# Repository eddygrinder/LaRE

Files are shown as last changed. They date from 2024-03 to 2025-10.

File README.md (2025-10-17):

## Objectives
This project is an integral part of the Master’s Dissertation entitled “LaRE – Expandable Remote Laboratory”.
It implements and manages a remote laboratory for electronics education, designed as a viable alternative to VISIR, with the additional commitment of being an open-source project, accessible to any educational institution regardless of geographical location.

The board matrix, the core element of the system, was developed based on a software-controlled architecture independent of proprietary platforms, ensuring that the system can be used without commercial licenses.

However, due to the current lack of support for the pyVirtualBench library on Linux systems and ARM architectures, the implementation of LaRE remains dependent on Windows systems — a factor that limits its adoption in more versatile and low-cost educational platforms.
Nevertheless, the modular architecture of LaRE enables future expansions and adaptations to different pedagogical contexts.

This dissertation partially fulfills the requirements defined in the Course Unit of Dissertation/Thesis of the 2nd year of the Master’s Degree in Electrical and Computer Engineering, specialization area in Automation and Systems.

## System Overview

The LaRE system is composed of:

* **PC (Server)** – runs a Flask-based Python web server.  
* **Raspberry Pi 5** – controls the relay matrix for switching circuits.  
* **NI VirtualBench (VB-8012)** – handles voltage, current, and waveform measurements.  
* **Web Interface** – implemented in HTML, CSS, and JavaScript for user interaction.  

Communication between the PC and Raspberry Pi is handled via **network sockets**, ensuring a simple and robust client–server connection.

## Helpful Resources
* [YouTube – Tech With Tim Flask Tutorial](https://www.youtube.com/watch?v=dam0GPOAvVI)  
* [Flask Official Documentation](https://flask.palletsprojects.com/en/stable/)  
* [pyVirtualBench Library (Armstrap)](https://github.com/armstrap/armstrap-pyvirtualbench)  
* [Armstrap Blog Post](http://armstrap.org/2015/07/27/pyvirtualbench-controlling-five-instruments-from-a-single-python-application/)

## Requirements (Windows Only)
* [NI VirtualBench hardware](http://www.ni.com/virtualbench/)
* [VirtualBench driver >= 1.1.0](https://www.ni.com/en-us/support/downloads/drivers/download.virtualbench-software.html#324215)
  Be sure to check "ANSI C Support" during installation.
    NiInstaller
* [Python >= 3.4](https://www.python.org/downloads/).  You will need 32-bit Python support to work with the NI-provided drivers.

## Dependencies
To install the Python dependencies:
* pip install -r requirements.txt

## Licensing
This project is distributed under the terms of the GNU General Public License, version 3 (GPLv3).
It includes portions of code adapted from: armstrap/armstrap-pyvirtualbench, licensed under the MIT License (© 2015 Charles Armstrap).

See the files LICENSE and THIRD_PARTY_LICENSES.txt for full details.

## Author
Eduardo Ramalhadeiro
Master’s in Electrical and Computer Engineering – Automation and Systems
Instituto Politécnico do Porto (ISEP)
© 2025

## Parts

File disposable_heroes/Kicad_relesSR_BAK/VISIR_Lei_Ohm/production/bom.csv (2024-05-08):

Designator | Footprint | Quantity | Value | LCSC Part #
C1 | C_Disc_D5.0mm_W2.5mm_P2.50mm | 1 | 0.1uF
J1 | PinHeader_2x20_P2.54mm_Vertical | 1 | Raspberry PI5
J10 | PinHeader_1x03_P2.54mm_Vertical | 1 | Amperimetro+
J11 | PinHeader_1x03_P2.54mm_Vertical | 1 | Amperimetro-
J2 | PinHeader_1x02_P2.54mm_Vertical | 1 | Fonte dc_VB
J3 | PinHeader_1x02_P2.54mm_Vertical | 1 | Fonte 12V
J4 | PinHeader_1x03_P2.54mm_Vertical | 1 | Voltimetro+
J5, J6, J7, J8 | PinHeader_1x20_P2.54mm_Vertical | 4 | Ext_OUT_PI
J9 | PinHeader_1x03_P2.54mm_Vertical | 1 | Voltimetro-
K1, K2, K3 | RELAY8_3572-1220-053_COM | 3 | 3572-1220-123
K4, K5, K6, K7, K8 | SIP_3570-1331_COM | 5 | 3570-1331-123
MES1 | PinHeader_1x02_P2.54mm_Vertical | 1 | Voltmeter_DC
MES3 | PinHeader_1x02_P2.54mm_Vertical | 1 | Ammeter_DC
R1 | R_Axial_DIN0207_L6.3mm_D2.5mm_P15.24mm_Horizontal | 1 | R1
R2 | R_Axial_DIN0207_L6.3mm_D2.5mm_P15.24mm_Horizontal | 1 | R2
R3 | R_Axial_DIN0207_L6.3mm_D2.5mm_P15.24mm_Horizontal | 1 | R3
U1 | DIP-16_W10.16mm | 1 | 74HC595N_112 | 74HC595N,112
U2, U3 | DIP-16_W10.16mm | 2 | ULN2003

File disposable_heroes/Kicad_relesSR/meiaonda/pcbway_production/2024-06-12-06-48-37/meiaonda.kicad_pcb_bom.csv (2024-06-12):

designator | quantity | value | pack | mpn | mount_type
C1 | 1 | 10uF | CP_Radial_D6.3mm_P2.50mm |  | tht
C2 | 1 | 100uF | CP_Radial_D6.3mm_P2.50mm |  | tht
C3, C4 | 2 | 0.1uF | C_Disc_D5.0mm_W2.5mm_P2.50mm |  | tht
C6 | 1 | 10uF | CP_Radial_D5.0mm_P2.00mm |  | tht
D1 | 1 | 1N4007 | D_DO-41_SOD81_P10.16mm_Horizontal |  | tht
D2 | 1 | B250C2300-1500A | Diode_Bridge_19.0x3.5x10.0mm_P5.0mm |  | tht
F1 | 1 | Fuse | Fuseholder_Cylinder-5x20mm_Stelvio-Kontek_PTF78_Horizontal_Open |  | tht
H1, H2, H3, H4 | 4 | MountingHole | MountingHole_3.2mm_M3 |  | tht
J2 | 1 | PI_config | PinSocket_1x06_P2.54mm_Vertical |  | tht
J3 | 1 | Power Sources | PinSocket_1x06_P2.54mm_Vertical |  | tht
J4 | 1 | Signals | PinSocket_1x06_P2.54mm_Vertical |  | tht
K1, K2, K3, K5, K6, K7, K8, K9 | 8 | 3572-1220-123 | RELAY8_3572-1220-053_COM |  | tht
K10, K11, K12, K13, K4 | 5 | 3570-1331-123 | SIP_3570-1331_COM |  | tht
R1, R3 | 2 | 1K | R_Axial_DIN0207_L6.3mm_D2.5mm_P15.24mm_Horizontal |  | tht
R2 | 1 | 4.7K | R_Axial_DIN0207_L6.3mm_D2.5mm_P15.24mm_Horizontal |  | tht
U1, U3 | 2 | 74HC595N_112 | DIP-16_W10.16mm | 74HC595N,112 | tht
U2, U4 | 2 | ULN2003 | DIP-16_W10.16mm |  | tht

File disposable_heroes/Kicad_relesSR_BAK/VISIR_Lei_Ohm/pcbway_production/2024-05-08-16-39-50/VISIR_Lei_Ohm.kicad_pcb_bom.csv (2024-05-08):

designator | quantity | value | pack | mpn | mount_type
C1 | 1 | 0.1uF | C_Disc_D5.0mm_W2.5mm_P2.50mm |  | tht
H1, H2, H3, H4 | 4 | MountingHole | MountingHole_3.2mm_M3 |  | tht
J1 | 1 | Raspberry PI5 | PinHeader_2x20_P2.54mm_Vertical |  | tht
J10 | 1 | Amperimetro+ | PinHeader_1x03_P2.54mm_Vertical |  | tht
J11 | 1 | Amperimetro- | PinHeader_1x03_P2.54mm_Vertical |  | tht
J2 | 1 | Fonte dc_VB | PinHeader_1x02_P2.54mm_Vertical |  | tht
J3 | 1 | Fonte 12V | PinHeader_1x02_P2.54mm_Vertical |  | tht
J4 | 1 | Voltimetro+ | PinHeader_1x03_P2.54mm_Vertical |  | tht
J5, J6, J7, J8 | 4 | Ext_OUT_PI | PinHeader_1x20_P2.54mm_Vertical |  | tht
J9 | 1 | Voltimetro- | PinHeader_1x03_P2.54mm_Vertical |  | tht
K1, K2, K3 | 3 | 3572-1220-123 | RELAY8_3572-1220-053_COM |  | tht
K4, K5, K6, K7, K8 | 5 | 3570-1331-123 | SIP_3570-1331_COM |  | tht
MES1 | 1 | Voltmeter_DC | PinHeader_1x02_P2.54mm_Vertical |  | tht
MES3 | 1 | Ammeter_DC | PinHeader_1x02_P2.54mm_Vertical |  | tht
R1 | 1 | R1 | R_Axial_DIN0207_L6.3mm_D2.5mm_P15.24mm_Horizontal |  | tht
R2 | 1 | R2 | R_Axial_DIN0207_L6.3mm_D2.5mm_P15.24mm_Horizontal |  | tht
R3 | 1 | R3 | R_Axial_DIN0207_L6.3mm_D2.5mm_P15.24mm_Horizontal |  | tht
U1 | 1 | 74HC595N_112 | DIP-16_W10.16mm | 74HC595N,112 | tht
U2, U3 | 2 | ULN2003 | DIP-16_W10.16mm |  | tht

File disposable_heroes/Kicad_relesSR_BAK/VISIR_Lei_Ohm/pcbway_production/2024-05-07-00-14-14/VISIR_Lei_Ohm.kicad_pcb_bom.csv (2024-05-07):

designator | quantity | value | pack | mpn | mount_type
C1, C2 | 2 | 0.1uF | C_Disc_D5.0mm_W2.5mm_P2.50mm |  | tht
H1, H2, H3, H4 | 4 | MountingHole | MountingHole_3.2mm_M3 |  | tht
J1 | 1 | Raspberry PI5 | PinHeader_2x20_P2.54mm_Vertical |  | tht
J2 | 1 | Fonte dc | PinHeader_1x02_P2.54mm_Vertical |  | tht
J3 | 1 | Fonte 12V | PinHeader_1x02_P2.54mm_Vertical |  | tht
J4 | 1 | Fonte 5V | PinHeader_1x02_P2.54mm_Vertical |  | tht
J5, J6, J7, J8 | 4 | Ext_OUT_PI | PinHeader_1x20_P2.54mm_Vertical |  | tht
K1, K2, K3 | 3 | 3572-1220-123 | RELAY8_3572-1220-053_COM |  | tht
K4, K5, K6, K7, K8 | 5 | 3570-1331-123 | SIP_3570-1331_COM |  | tht
MES1 | 1 | Voltmeter_DC | PinHeader_1x02_P2.54mm_Vertical |  | tht
MES3 | 1 | Ammeter_DC | PinHeader_1x02_P2.54mm_Vertical |  | tht
R1 | 1 | R1 | R_Axial_DIN0207_L6.3mm_D2.5mm_P15.24mm_Horizontal |  | tht
R2 | 1 | R2 | R_Axial_DIN0207_L6.3mm_D2.5mm_P15.24mm_Horizontal |  | tht
R3 | 1 | R3 | R_Axial_DIN0207_L6.3mm_D2.5mm_P15.24mm_Horizontal |  | tht
U1, U4 | 2 | 74HC595N_112 | DIP-16_W10.16mm | 74HC595N,112 | tht
U2, U3 | 2 | ULN2003 | DIP-16_W10.16mm |  | tht

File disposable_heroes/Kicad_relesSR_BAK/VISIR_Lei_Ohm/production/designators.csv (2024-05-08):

C1:1
H1:1
H2:1
H3:1
H4:1
J1:1
J10:1
J11:1
J2:1
J3:1
J4:1
J5:1
J6:1
J7:1
J8:1
J9:1
K1:1
K2:1
K3:1
K4:1
K5:1
K6:1
K7:1
K8:1
MES1:1
MES3:1
R1:1
R2:1
R3:1
U1:1
U2:1
U3:1

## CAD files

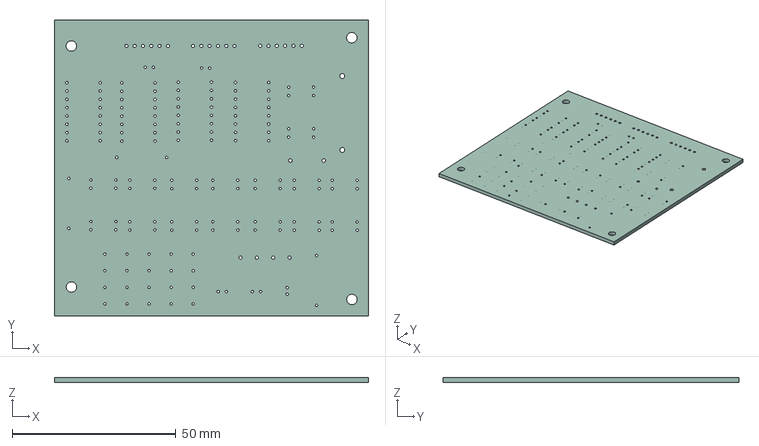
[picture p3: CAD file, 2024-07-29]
disposable_heroes/Kicad_relesSR/meiaonda/meiaonda.step
96.0 x 90.5 x 1.60 mm

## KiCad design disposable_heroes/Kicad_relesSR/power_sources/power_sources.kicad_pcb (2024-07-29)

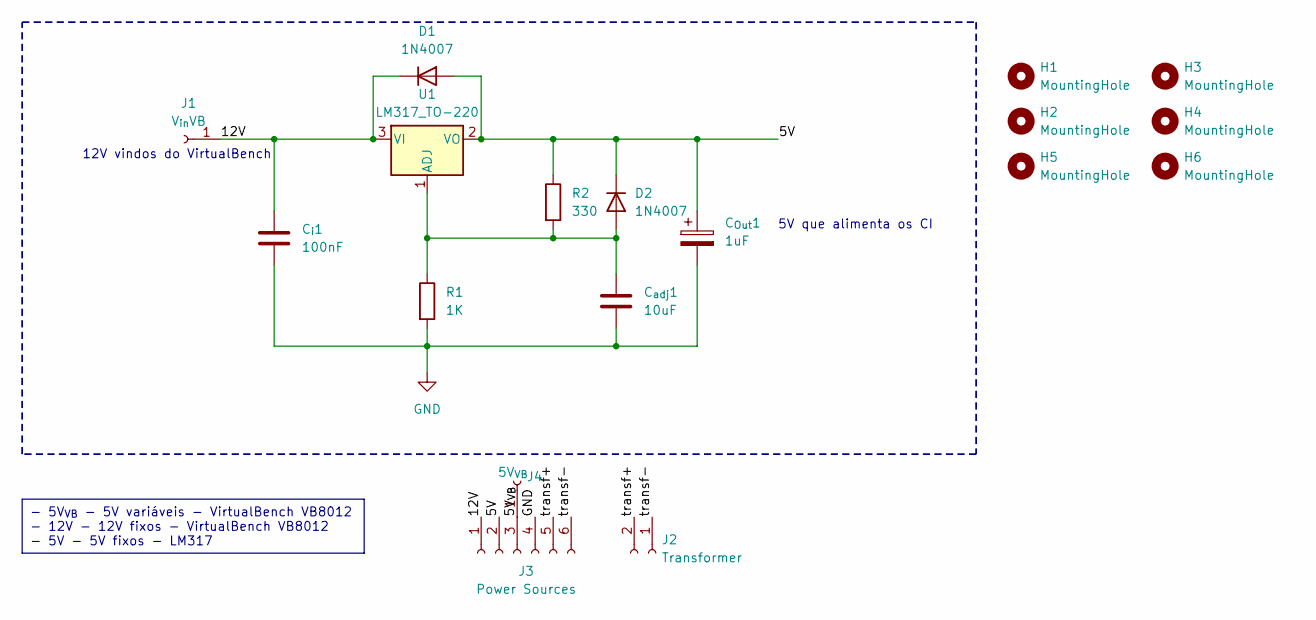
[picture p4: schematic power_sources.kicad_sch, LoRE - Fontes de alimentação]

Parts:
C_{Out}1: 1uF; CP_Radial_D5.0mm_P2.00mm
C_{adj}1: 10uF; CP_Radial_D5.0mm_P2.00mm
C_{i}1: 100nF; C_Disc_D5.1mm_W3.2mm_P5.00mm
D1, D2: 1N4007; D_DO-41_SOD81_P10.16mm_Horizontal
H1, H2, H3, H4, H5, H6: MountingHole; MountingHole_3.2mm_M3
J1: V_{in}VB; PinSocket_1x01_P2.54mm_Vertical
J2: Transformer; PinSocket_1x02_P2.54mm_Vertical
J3: Power Sources; PinSocket_1x06_P2.54mm_Vertical
J4: 5V_{VB}; PinSocket_1x01_P2.54mm_Vertical
R1: 1K; R_Axial_DIN0207_L6.3mm_D2.5mm_P15.24mm_Horizontal
R2: 330; R_Axial_DIN0207_L6.3mm_D2.5mm_P15.24mm_Horizontal
U1: LM317_TO-220; TO-220-3_Vertical

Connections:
/5V: C_{Out}1.1, D1.2 (A), D2.1 (K), J3.2, R2.1, U1.2 (VO)
/5V_{VB}: J3.3, J4.1
/12V: C_{i}1.1, D1.1 (K), J1.1, J3.1, U1.3 (VI)
/transf+: J2.2, J3.5
/transf-: J2.1, J3.6
GND: C_{Out}1.2, C_{adj}1.2, C_{i}1.2, J3.4, R1.2
unnamed: C_{adj}1.1, D2.2 (A), R1.1, R2.2, U1.1 (ADJ)

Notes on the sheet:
- 5V_{VB} - 5V variáveis - VirtualBench VB8012 - 12V - 12V fixos - VirtualBench VB8012 - 5V - 5V fixos - LM317
5V que alimenta os CI
12V vindos do VirtualBench

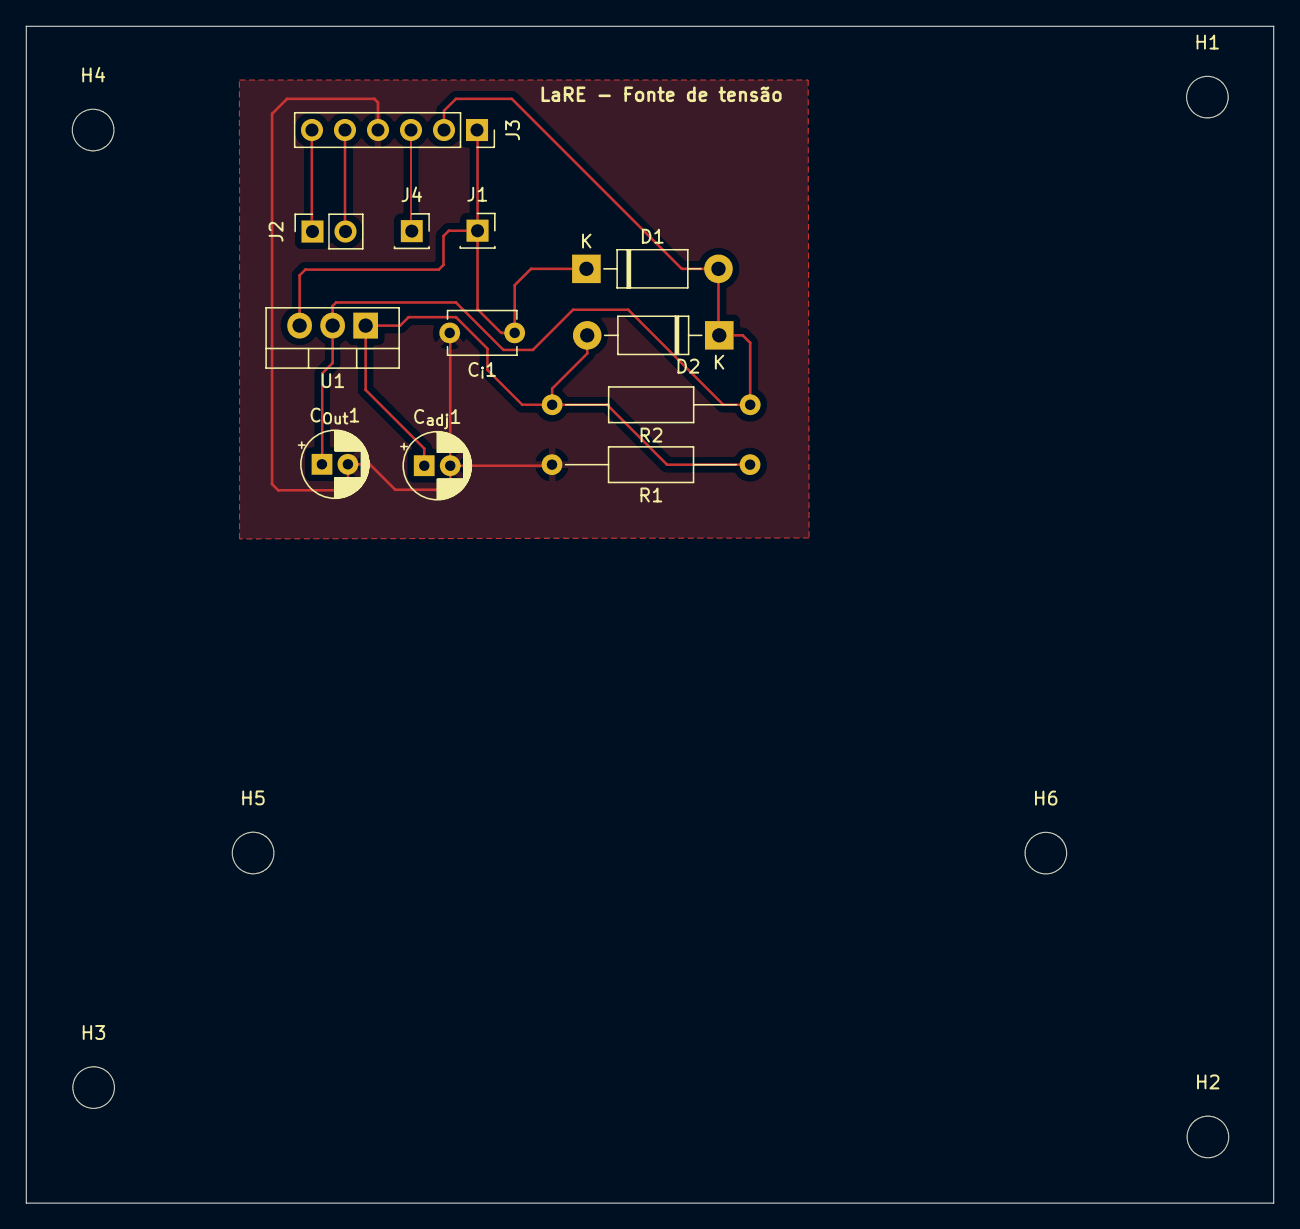
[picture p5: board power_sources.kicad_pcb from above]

Board: 4 copper layers, 96.0 x 90.6 mm, 18 parts (0 on the bottom side), 7 nets.

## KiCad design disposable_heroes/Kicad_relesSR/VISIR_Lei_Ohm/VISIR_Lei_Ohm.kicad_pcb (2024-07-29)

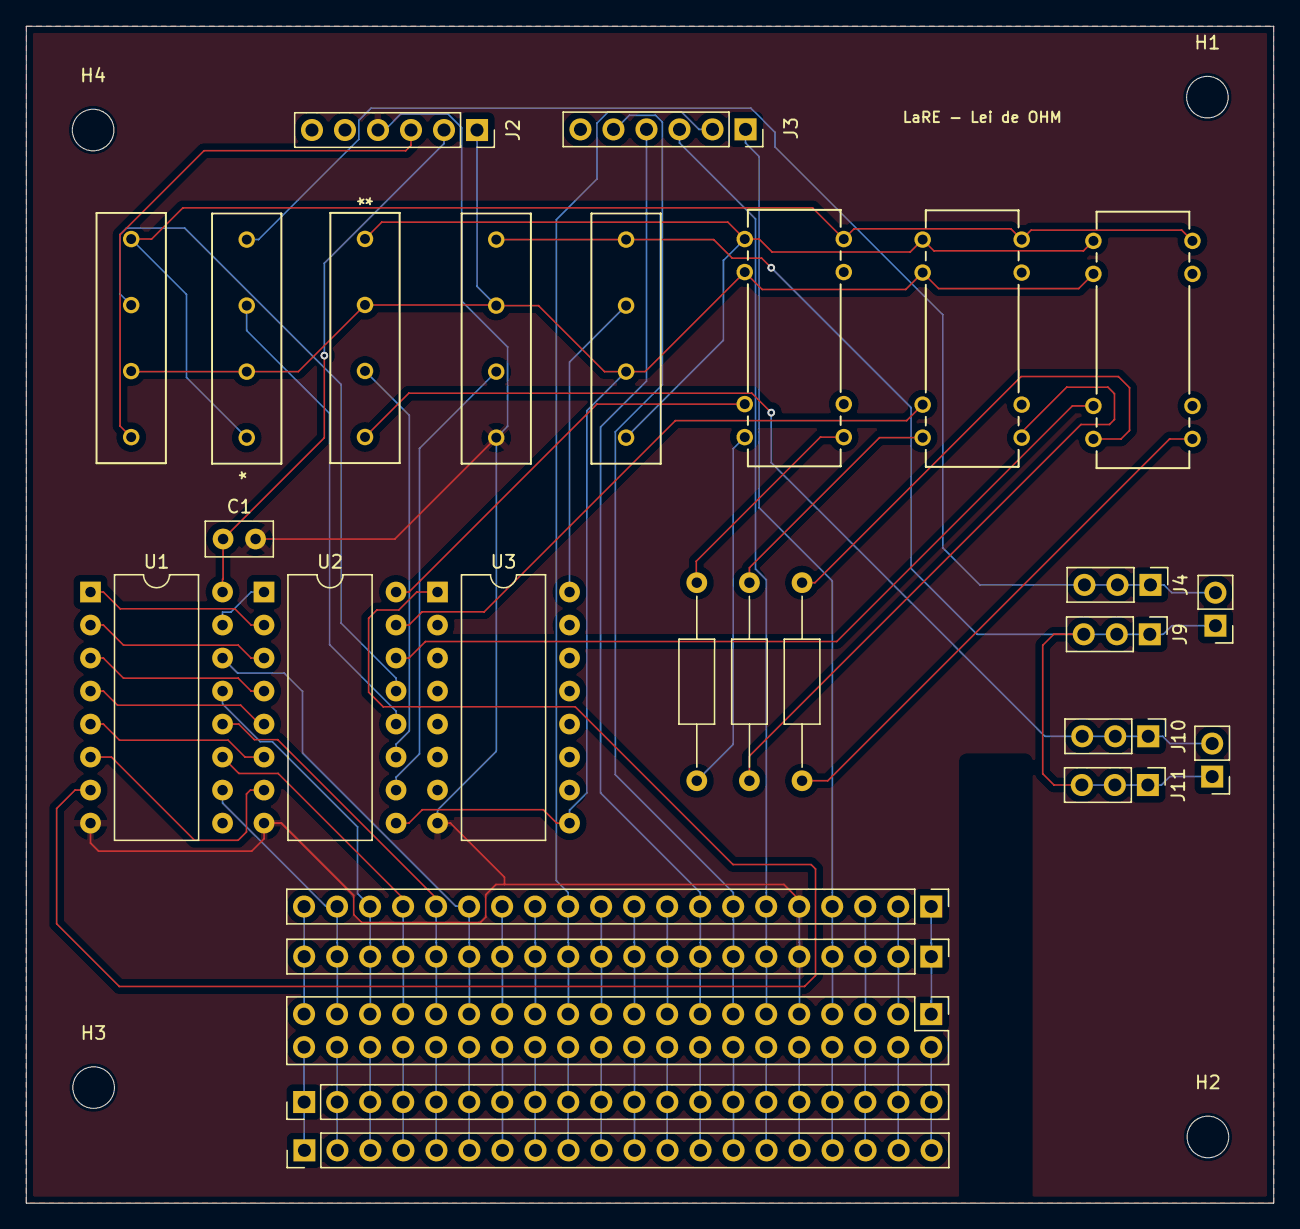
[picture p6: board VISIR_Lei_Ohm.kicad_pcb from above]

Board: 2 copper layers, 96.0 x 90.5 mm, 32 parts (0 on the bottom side), 70 nets.

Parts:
C1: 0.1uF; C_Disc_D5.0mm_W2.5mm_P2.50mm
H1, H2, H3, H4: MountingHole; MountingHole_3.2mm_M3
J1: Raspberry PI5; PinHeader_2x20_P2.54mm_Vertical
J2: Power Sources; PinSocket_1x06_P2.54mm_Vertical
J3: PI_config; PinSocket_1x06_P2.54mm_Vertical
J4: Voltimetro+; PinHeader_1x03_P2.54mm_Vertical
J5, J6, J7, J8: Ext_OUT_PI; PinHeader_1x20_P2.54mm_Vertical
J9: Voltimetro-; PinHeader_1x03_P2.54mm_Vertical
J10: Amperimetro+; PinHeader_1x03_P2.54mm_Vertical
J11: Amperimetro-; PinHeader_1x03_P2.54mm_Vertical
K1, K2, K3: 3572-1220-123; RELAY8_3572-1220-053_COM
K4, K5, K6, K7, K8: 3570-1331-123; SIP_3570-1331_COM
MES1: Voltmeter_DC; PinHeader_1x02_P2.54mm_Vertical
MES3: Ammeter_DC; PinHeader_1x02_P2.54mm_Vertical
R1: R1; R_Axial_DIN0207_L6.3mm_D2.5mm_P15.24mm_Horizontal
R2: R2; R_Axial_DIN0207_L6.3mm_D2.5mm_P15.24mm_Horizontal
R3: R3; R_Axial_DIN0207_L6.3mm_D2.5mm_P15.24mm_Horizontal
U1: 74HC595N_112; DIP-16_W10.16mm
U2, U3: ULN2003; DIP-16_W10.16mm

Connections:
/5V: C1.1, J2.2, U1.16 (VCC)
/5VPower1: J1.2 (5VPower1), J5.20, J6.20
/5V_{VB}: J2.3, K4.1
/12V: J2.1, K1.2, K2.2, K3.2, K4.2, K5.2, K6.2, K7.2, K8.2, U2.9 (COM), U3.9 (COM)
/I_{11}: U1.15 (Q0), U2.1 (I1)
/I_{12}: U1.1 (Q1), U2.2 (I2)
/I_{13}: U1.2 (Q2), U2.3 (I3)
/I_{14}: U1.3 (Q3), U2.4 (I4)
/I_{15}: U1.4 (Q4), U2.5 (I5)
/I_{16}: U1.5 (Q5), U2.6 (I6)
/I_{17}: U1.6 (Q6), U2.7 (I7)
/I_{21}: U1.7 (Q7), U3.1 (I1)
/O_{11}: K1.6, U2.16 (O1)
/O_{12}: K2.6, U2.15 (O2)
/O_{13}: K3.6, U2.14 (O3)
/O_{14}: K4.3, U2.13 (O4)
/O_{15}: K5.3, U2.12 (O5)
/O_{16}: K6.3, U2.11 (O6)
/O_{17}: K7.3, U2.10 (O7)
/O_{21}: K8.3, U3.16 (O1)
/RCLK: J1.31 (GPIO6), J7.16, J8.16, U1.12 (RCLK)
/RCLK_{filters}: J1.11 (GPIO17), J3.3, J7.6, J8.6
/SER1: J1.29 (GPIO5), J7.15, J8.15, U1.14 (SER)
/SER_{filters}: J1.13 (GPIO27), J3.5, J7.7, J8.7
/SRCLK: J1.33 (GPIO13/PWM1), J7.17, J8.17, U1.11 (SRCLK)
/SRCLK_{filters}: J1.7 (GPIO4/GPCLK0), J3.1, J7.4, J8.4
/~OE: J1.35 (GPIO19/PCM_FS), J7.18, J8.18, U1.13 (~OE)
/~OE_{filters}: J1.15 (GPIO22), J3.4, J7.8, J8.8
/~SRCLR: J1.37 (GPIO26), J7.19, J8.19, U1.10 (~SRCLR)
/~SRCLR_{filters}: J1.23 (GPIO11/SCLK), J3.2, J7.12, J8.12
A: K1.14, K2.14, K3.14, K4.4, K5.1
B: K1.1, K2.1, K3.1, K6.1, K8.1
C: J9.1, J9.2, J9.3, J11.1, J11.2, J11.3, K7.1, K8.4, MES1.1 (-), MES3.1 (-)
GND: C1.2, J1.9 (GND), J2.4, J7.5, J8.5, K7.4, U1.8 (GND), U2.8 (GND), U3.8 (GND)
GND1: J1.25 (GND), J7.13, J8.13
GND2: J1.39 (GND), J7.20, J8.20
GND3: J1.6 (GND), J5.18, J6.18
GND4: J1.14 (GND), J5.14, J6.14
GND5: J1.20 (GND), J5.11, J6.11
GND6: J1.30 (GND), J5.6, J6.6
GND7: J1.34 (GROUND), J5.4, J6.4
unnamed: J1.1 (3V3Power1), J7.1, J8.1
unnamed: J1.17 (3v3Power2), J7.9, J8.9
unnamed: J1.4 (5VPower2), J5.19, J6.19
unnamed: J1.27 (GPIO0/ID_SD), J7.14, J8.14
unnamed: J1.28 (GPIO1/ID_SC), J5.7, J6.7
unnamed: J1.3 (GPIO2/SDA), J7.2, J8.2
unnamed: J1.5 (GPIO3/SCL), J7.3, J8.3
unnamed: J1.26 (GPIO7/CE1), J5.8, J6.8
unnamed: J1.24 (GPIO8/CE0), J5.9, J6.9
unnamed: J1.21 (GPIO9/MISO), J7.11, J8.11
unnamed: J1.19 (GPIO10/MOSI), J7.10, J8.10
unnamed: J1.32 (GPIO12/PWM0), J5.5, J6.5
unnamed: J1.8 (GPIO14/TXD), J5.17, J6.17
unnamed: J1.10 (GPIO15/RXD), J5.16, J6.16
unnamed: J1.36 (GPIO16), J5.3, J6.3
unnamed: J1.12 (GPIO18/PCM_CLK), J5.15, J6.15
unnamed: J1.38 (GPIO20/PCM_DIN), J5.2, J6.2
unnamed: J1.40 (GPIO21/PCM_DOUT), J5.1, J6.1
unnamed: J1.16 (GPIO23), J5.13, J6.13
unnamed: J1.18 (GPIO24), J5.12, J6.12
unnamed: J1.22 (GPIO25), J5.10, J6.10
unnamed: J4.1, J4.2, J4.3, K5.4, MES1.2 (+)
unnamed: J10.1, J10.2, J10.3, K6.4, MES3.2 (+)
unnamed: K1.7, R1.1
unnamed: K1.8, R1.2
unnamed: K2.7, R2.2
unnamed: K2.8, R2.1
unnamed: K3.7, R3.2
unnamed: K3.8, R3.1

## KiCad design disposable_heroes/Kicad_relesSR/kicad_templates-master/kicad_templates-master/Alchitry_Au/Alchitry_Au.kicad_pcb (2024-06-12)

Board: 2 copper layers, 8 parts (0 on the bottom side), 3 nets, no tracks yet.

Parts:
B1, B2, B3, B4: Alchitry_Shield; Alchitry_Conn
H1, H2, H3, H4: MountingHole; 2m2ThroughHole

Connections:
+3V3: B1.B7, B1.B13, B1.B19, B1.B25, B1.B26, B1.B32, B1.B38, B1.B44, B2.B7, B2.B13, B2.B19, B2.B25, B2.B26, B2.B32, B2.B38, B2.B44, B3.B7, B3.B13, B3.B19, B3.B25, B3.B26, B3.B32, B3.B38, B3.B44, B4.B7, B4.B13, B4.B19, B4.B25, B4.B26, B4.B32, B4.B38, B4.B44
+5V: B1.B1, B1.B50, B2.B1, B2.B50, B3.B1, B3.B50, B4.B50
GND: B1.B4, B1.B10, B1.B16, B1.B22, B1.B29, B1.B35, B1.B41, B1.B47, B2.B4, B2.B10, B2.B16, B2.B22, B2.B29, B2.B35, B2.B41, B2.B47, B3.B4, B3.B10, B3.B16, B3.B22, B3.B29, B3.B35, B3.B41, B3.B47, B4.B4, B4.B10, B4.B16, B4.B22, B4.B29, B4.B35, B4.B41, B4.B47

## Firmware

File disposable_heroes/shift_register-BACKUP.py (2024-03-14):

import RPi.GPIO as GPIO

#GPIO Mode (BOARD / BCM)
GPIO.setmode(GPIO.BCM)

import serial
import time

import sys
import cv2

import schemdraw
import schemdraw.elements as elm

import subprocess

# Resistencias:
# R1 = 470
# R2 = 1.2K
# R3 = 10K

SER = 5         # GPIO 5 - SER/DS (serial data input, SPI data)
RCLK = 6        # GPIO 6 - RCLK/STCP
SRCLK = 13      # GPIO 13 - SRCLK/SHCP (storage register clock pin, SPI clock)
SRCLR = 26      # GPIO 26 - O registo de deslocamento é limpo (ACTIVO BAIXO)

# Setup dos pinos
GPIO.setup(SER, GPIO.OUT)               
GPIO.setup(RCLK, GPIO.OUT)                     
GPIO.setup(SRCLOCK, GPIO.OUT)
GPIO.setup(SRCLR, GPIO.OUT)

# Inicializar a variavel correspondente a R1
# Reles 1 e 2
rele_1_2 = b0011

# Valor por defeito de espera nas operações do registo de deslocamento
WaitTimeSR = 0.1

# Inicaializa o pino de clear dos registos a 1 - o clear é controlado e feito numa função
GPIO.output(SRCLR, 1)


# Caminho para o visualizador de imagens (pode variar dependendo do seu sistema operacional)
visualizador = "xdg-open"  # Linux
# visualizador = "open"  # macOS
# vi

import warnings
warnings.filterwarnings("ignore")

#arduino = serial.Serial (port='/dev/ttyACM1', baudrate='9600')
#time.sleep(2)

# Caminho para o visualizador de imagens (pode variar dependendo do seu sistema operacional)
visualizador = "xdg-open"  # Linux
# visualizador = "open"  # macOS
# visualizador = "start"  # Windows

def main():
    # Escolha do valor da resistência
    # Não sai do ciclo enquanto não for feita uma escolha válida
    print("Para o estudo da Lei de Ohm escolha uma das três resistências:")
    print("- 470 Ohm")
    print ("- 1.2K")
    print ("- 10K")

    while True:
        try:
            R1_Value = input("Escolha o valor da Resistência - ")

            # Validação da escolha
            if R1_Value in ("470", "1K2", "10K"):
                caminho_imagem = "esquemaOhm.png"
                subprocess.Popen([visualizador, caminho_imagem])
                draw_schematic(R1_Value)
                # Enviar os bits para o Shift register e activar os relés 
                register_clear() # Efectua a limpeza do registo
                SRoutput(rele_1_2)
                break
            else:
                raise ValueError("Escolha não é válida")
        except ValueError as e:
            print(e)    


#if (escolha == 'R1'):
#print("escolheu R1")
#cv2.destroyAllWindows() # destroy all windows
#byte_R1 = "004002000000\n"
#arduino.write(byte_R1.encode())
#time.sleep(0.5)
#arduino.close

def draw_schematic(R1_Value):
    with schemdraw.Drawing(show=False) as d:
        d.config(unit=5) #tamanho do componente
        # Adicionando os elementos
        d += (V1 := elm.SourceV().label('Vin'))
        d += (I1 := elm.MeterA().right().label('Amp'))
        d += elm.Dot()
        d.push()
        d += (R1 := elm.Resistor().down().label(R1_Value, loc='bot'))
        d += elm.Dot()
        d.pop()
        d += (L1 := elm.Line())
        d += (Vol := elm.MeterV().down().label('Volt', loc='bot', rotate=True))
        d += (L2 := elm.Line().tox(V1.start))            
        #d.draw()
        d.save('esquemaOhm.png')

# Funcao que limpa o registo
def register_clear ()
    GPIO.output(SRCLR, 0) # É feito o clear
    time.sleep(waitTimeSR) # espera 100ms
    GPIO.output(SRCLR, 1)

# Função que verifica e desloca os bits para armazenar no registo de deslocamento
def SRoutput(bit_Reles):
    for i in range(4):
        checkshift = shiftnum & 1
        if checkshift == 1:
            WriteReg (checkshift, WaitTimeSR)
        else:
            WriteReg(checkshift, WaitTimeSR)
    shiftnum = shiftnum >> 1


# Definição da função que envia os dados para o registo de deslocamento,
# segundo o algoritmo descrito em baixo

### ALGORITMO ###
# Enviar um bit para o pino SER/DS
### Depois de enviado, é dado um impulso de clock (SRCLK/SHCP) e o bit armazenado nos registos
###### ... um segundo bit é enviado, repetindo os dois passos em cima - É repetido até estarem armazenados 8 bits
######### Por ultimo é dado um impulso aos registos (RCLK/STCP) para obter os 8 bits na saida

def WriteReg (WriteBit, WaitTimeSR):
    GPIO.output (SER,WriteBit) # Envia o bit 1 para o registo
    # Clock - flanco POSITIVO
    time.sleep (WaitTimeSR) # Espera 100ms
    GPIO.output(SRCLK, 0)
    time.sleep (WaitTimeSR) # Espera 100ms
    GPIO.output(SRCLK,1)
    time.sleep(WaitTimeSR) # Espera 100ms
    # Armazenar o valor no registo
    GPIO.output(RCLK, 0)
    time.sleep(WaitTimeSR) # Espera 100ms
    GPIO.output(RCLK, 1)

if __name__ == "__main__":
    main()

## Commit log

2024-04-05 update leituras continuas do virtualbench Foi criado um novo arquivo para armazenar as leituras do virtualbench e do dmm, para que seja possível acessar esses valores de qualquer lugar do código.
2024-04-07 Voltage/Current done Graphic interface NOT done
    [VISIR_Lei_Ohm.kicad_sch]
2024-04-27 update kicad
    [VISIR_Lei_Ohm.kicad_pcb, VISIR_Lei_Ohm.kicad_sch, bom.csv, designators.csv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]
2024-05-04 update meia onda - image
    [meiaonda.kicad_pcb, meiaonda.kicad_sch]
2024-05-07 massive update from laptop to PC
    [VISIR_Lei_Ohm-B_Cu.gbr, VISIR_Lei_Ohm-B_Mask.gbr, VISIR_Lei_Ohm-B_Paste.gbr, VISIR_Lei_Ohm-B_SilkS.gbr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]
2024-05-08 update kicad meia onda
    [VISIR_Lei_Ohm.kicad_pcb, VISIR_Lei_Ohm.kicad_sch, meiaonda.kicad_pcb, meiaonda.kicad_sch]
2024-05-08 update kicad meiaonda e ohm
    [VISIR_Lei_Ohm-B_Cu.gbr, VISIR_Lei_Ohm-B_Mask.gbr, VISIR_Lei_Ohm-B_Paste.gbr, VISIR_Lei_Ohm-B_SilkS.gbr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]
2024-05-15 update more circuits
    [meiaonda.kicad_pcb, meiaonda.kicad_sch]
2024-05-28 update error capacitor 74595
2024-05-31 update onda completa
    [meiaonda.kicad_sch]
2024-06-05 problemas com o onda completa
    [meiaonda.kicad_sch]
2024-06-05 Rectificador de onda completa a funcionar, somente com o canal 1 ligado à saída, aparentemente, não funciona só com o canal 2
    [meiaonda.kicad_sch]
2024-06-06 adiocionado relé K13, para cortar o sinal para a meia onda
    [meiaonda.kicad_sch]
2024-06-06 minor update kicad
    [meiaonda.kicad_sch]
2024-06-11 start low pass filter
    [meiaonda.kicad_sch]
2024-06-12 update - boards done
    [AISLER-2Layer.kicad_pcb, AISLER-2Layer.sch, AISLER-4Layer.kicad_pcb, AISLER-4Layer.sch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]
2024-06-12 updates finais
    [VISIR_Lei_Ohm.kicad_pcb, power_sources.kicad_pcb, power_sources.kicad_sch]
2024-07-29 update kicad files
    [VISIR_Lei_Ohm.kicad_pcb, VISIR_Lei_Ohm.kicad_sch, meiaonda.kicad_sch, meiaonda.step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]
2024-08-13 update esquema simplificado
    [esquema_simplificado_OHM.kicad_pcb, esquema_simplificado_OHM.kicad_sch]
2024-08-16 Adicionado flowchart_OHM.drawio
2024-08-16 Actualizar flowchart_OHM.drawio
2024-08-20 update: ficheiro diagram, flowchart. Actualização LaRE
2025-02-01 Adicionado circuit_R1.drawio
2025-02-01 Actualizar circuit_R1.drawio
2025-02-01 Adicionado circuit_R1.png
2025-02-04 update - uniformização das imagens feitas com o KICAD
    [esquemas_relatorio.kicad_pcb, esquemas_relatorio.kicad_sch]
2025-02-05 Finished - uniformização paginas HTML
    [esquemas_relatorio.kicad_sch]
2025-02-21 minor update - chamada de atenção no ficheiro ohm.html
2025-04-16 update images, diagrams
    [esquemas_relatorio.kicad_sch]
2025-04-17 UPDATE IMPORTANTE - rectificação de meia onda está a funcionar, o ficheiro correcto e que NÃO SE DEVE APAGAR é o mixed_signal_osciloscope_FUNCA
2025-04-24 24/04 - tudo aparentemente a funcionar. Falta o rectificador de onda completa e o relé K9 não funciona - ligação entre o registo e o driver. Os nomes dos ficheiros também não estão bem
2025-05-12 12-05 - Onda completa, funciona somente a onda de saída
2025-05-12 12-05 - aparentemente tudo a funcionar com a onda completa. NO ENTANTO, ainda há problemas de estabilidade no que diz respeito ao gráfico da onda de entrada
2025-06-07 Reles na onda completa têm de ser activados dentro do mixed_signal...
2025-06-12 13-06: software muito instável para medir e apresentar as duas ondas - in e ou. optou-se por medir e apresentar só a saída
    [meiaonda.kicad_sch]
2025-06-14 FUNCA - alguns prints apagados
2025-06-16 UPDATE - O sinal de saída do ripple de onda completa, foi suavizado usando o filtro descrito nos comentários
2025-10-15 UPDATE: passa alto e pasa baixo com informação de espera na visualização do gráfico
2025-10-17 removidos comentários e reduzido tempo para 0.2
2025-10-19 final de comentários
